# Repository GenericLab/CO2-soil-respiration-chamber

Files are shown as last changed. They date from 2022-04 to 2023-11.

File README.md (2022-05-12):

# CO2-soil-respiration-chamber

For more info of our developments and field testing, visit the hackeria wiki: https://www.hackteria.org/wiki/CO2_Soil_Respiration_Chamber

Visit our live data on Thingspeak: https://thingspeak.com/channels/1718702

## Make your own hardware

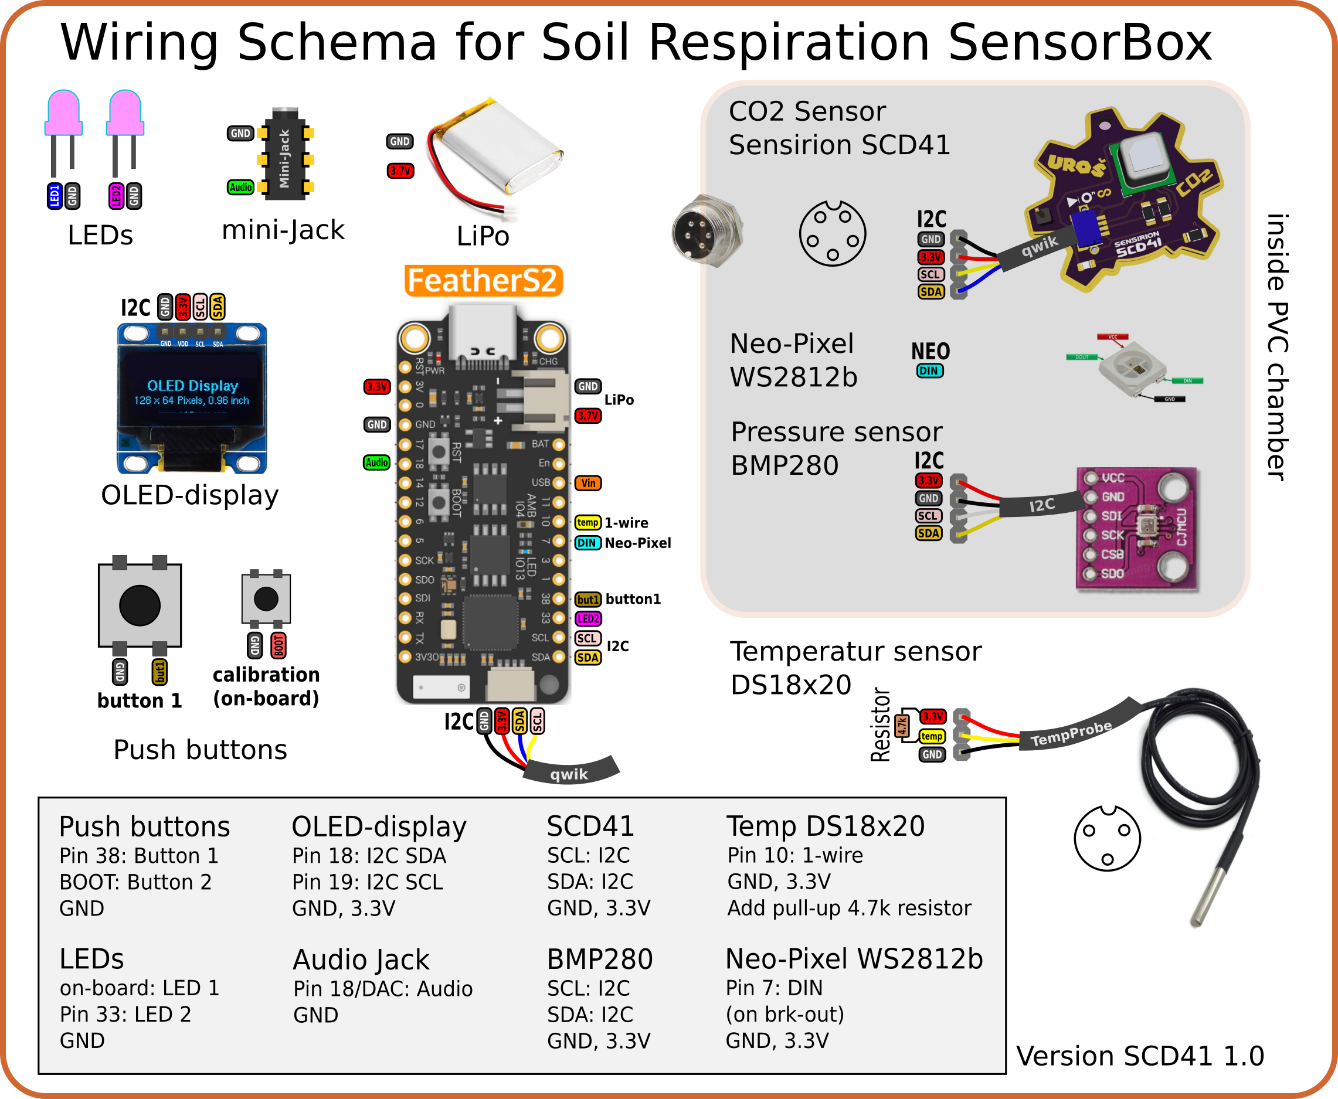
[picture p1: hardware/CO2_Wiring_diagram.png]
wiring diagram


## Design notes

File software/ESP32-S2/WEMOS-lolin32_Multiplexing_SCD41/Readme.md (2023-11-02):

This program allows to use up to four SCD41 with a Wemos lolin32 lite board for up to four soil respiration chambers to be running simultaneously, it includes the usage of a OLED screen as User Interface, a BMP280 sensor for altitude calibration, and data sending to two thingspeak channels.

The wiring is as shown next

Wemos_Schematics

You can acces the electrical details and PCB terminals count in the next file:
[Terminals Count](https://github.com/GenericLab/CO2-soil-respiration-chamber/blob/main/hardware/WEMOS-lolin32_Multiplexing_SCD41%20schematics/Terminals%20Count.xlsx)

The Soil respiration chamber contains a SCD41 sensor as shown next:

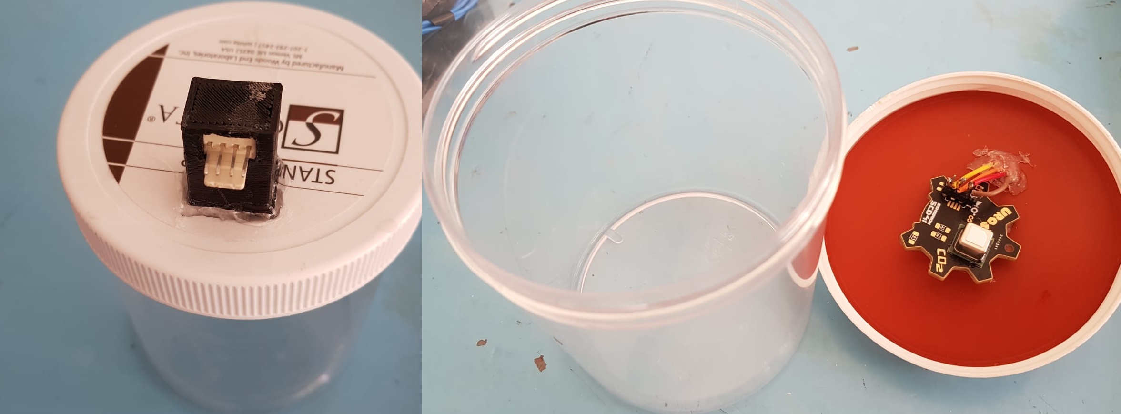
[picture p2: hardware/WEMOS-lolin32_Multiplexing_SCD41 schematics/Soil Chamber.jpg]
Soil Chamber 1


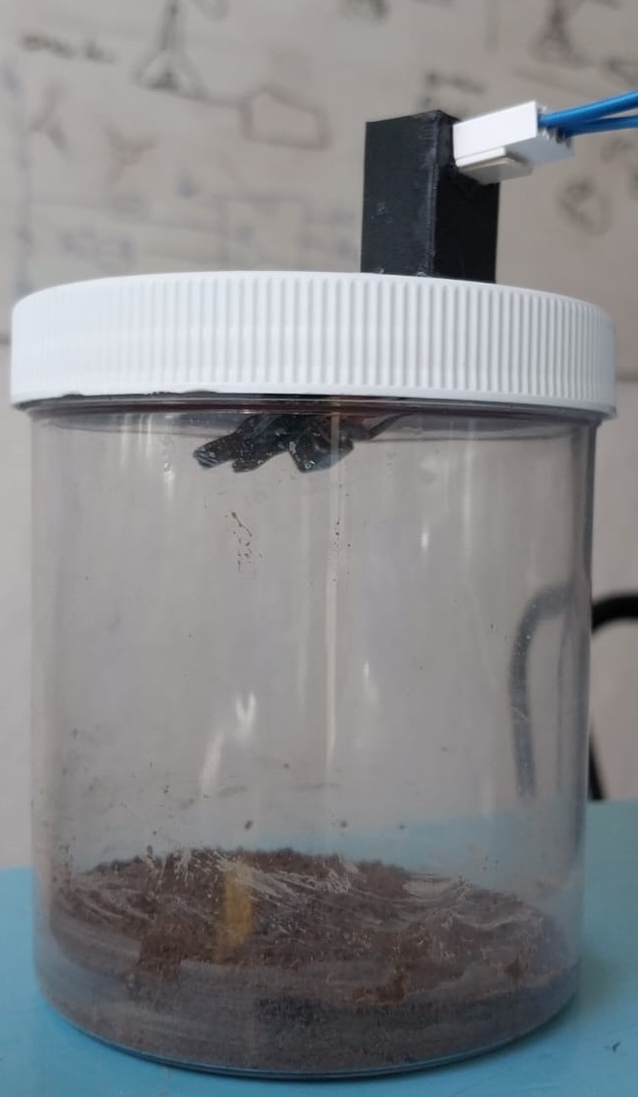
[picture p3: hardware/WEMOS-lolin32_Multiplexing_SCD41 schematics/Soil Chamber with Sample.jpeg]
Soil Chamber 2


The Cabinet that contains the rest of the electronics as shown next:

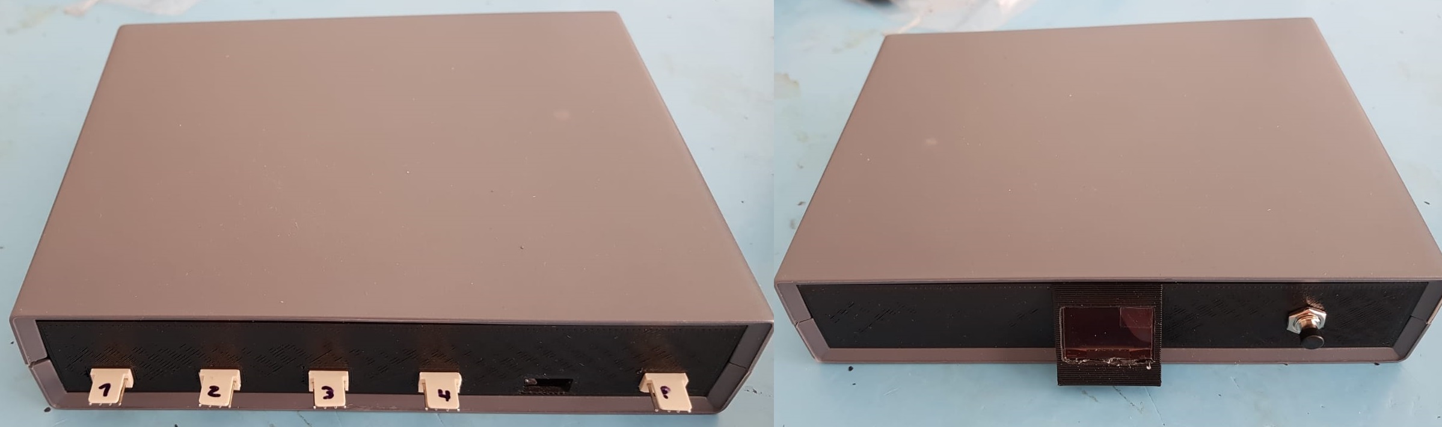
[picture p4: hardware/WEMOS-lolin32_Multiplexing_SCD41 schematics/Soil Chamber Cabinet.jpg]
Soil Chamber Cabinet 1


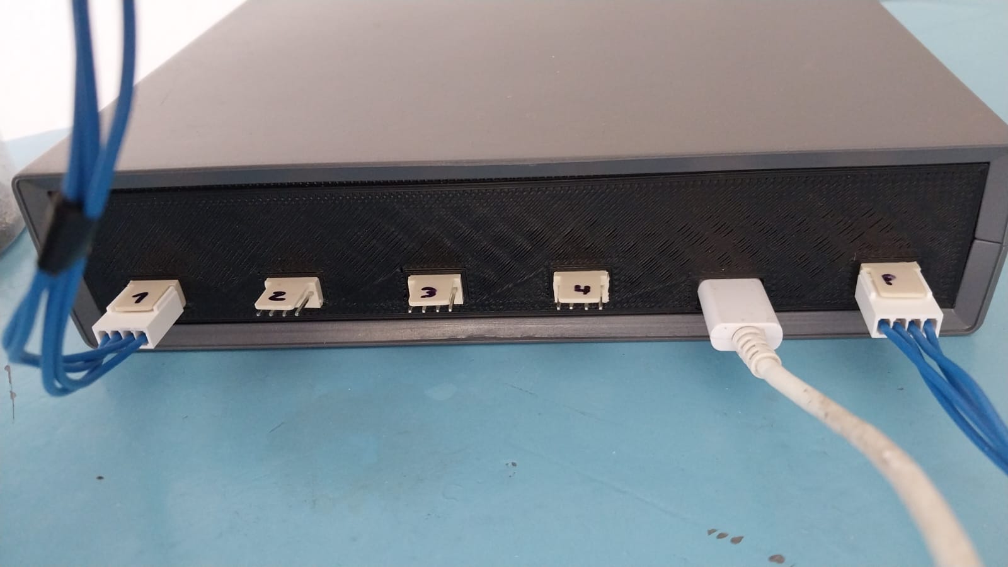
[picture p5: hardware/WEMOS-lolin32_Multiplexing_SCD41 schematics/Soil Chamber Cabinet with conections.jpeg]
Soil Chamber Cabinet 2


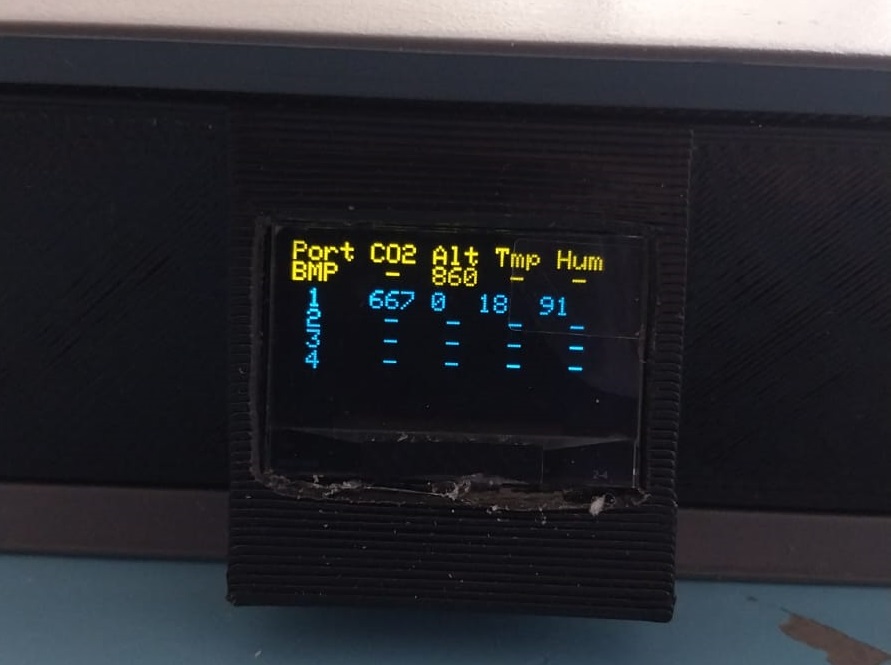
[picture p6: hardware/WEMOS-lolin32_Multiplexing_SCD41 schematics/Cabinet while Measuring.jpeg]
Soil Chamber Cabinet 3


The Wemos detects the sensors at setup, so you need to power the box after connecting the BMP280 (if available) and the SCD41 sensor

To start using the soil chamber you'll need to calibrate the sensor first. Then you shall weight 30 grams of the sample and slowly add 9 mililiters of water trying to hydrate most of the soil. Then you'll close the container and let it measuring the CO2 concentration, it is highly recomended to not turn off the readings, because the SCD41 can lose calibration when turned off.

The calibration procedure starts when the button is pressed for 5 seconds, this is for avoiding accidental pushes of the button such as bounce of vibrations. For calibration to be successfull you'll need to open the respiration chamber and expose the sensor and the chamber to fresh air, then push the buton so the sensor start to measure fresh air, it gets calibrated using the air pressure given by the BMP sensor if available, or the Lujan de Cuyo Altitude variable in SCD41_multiplexed.h file (you can change the used altitude in the main file istead of BMP readings if you need to). The full process last 3 to 4 minutes. After it's finished the sensor CO2 measurement is calibrated to 400 PPM, it is important to note that this is not an absolute measurement, but a relative one.

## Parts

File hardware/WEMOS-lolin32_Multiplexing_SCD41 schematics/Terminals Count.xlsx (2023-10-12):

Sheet: Terminals
 | Ground Pins | 3.3V Pins | I2C SCD Pins | I2C SDA Pins
Wemos Lolin32 Lite | 1 | 1 | 1 | 1
SCD41 | 4 | 4
Screen | 1 | 1 | 1 | 1
TCA9548A | 1 | 1 | 1 | 1
HW611 BMP280 | 1 | 1 | 1 | 1
Button | 1
 |  |  |  |  | Total
Total | 9 | 8 | 4 | 4 | 25

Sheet: Currents
 | mA | Quantity | Total mA | Fuente | Pagina
SCD41 | 15 | 4 | 60 | https://pdf1.alldatasheet.com/datasheet-pdf/view/1425096/SENSIRION/SCD41.html | 4
GME12864-43 | 12.3 | 1 | 12.3 | https://www.buydisplay.com/download/manual/ER-OLED0.96-1_Series_Datasheet.pdf | 14
TCA9548A | 0.05 | 1 | 0.05 | https://pdf1.alldatasheet.com/datasheet-pdf/view/463225/TI1/TCA9548A.html | 10
HW611 BMP280 | 0.0028 | 1 | 0.0028 | https://pdf1.alldatasheet.com/datasheet-pdf/view/1132069/BOSCH/BMP280.html | 7
 |  | Total | 72.3528
esp32 | 600 |  |  | https://learn.sparkfun.com/tutorials/esp32-thing-hookup-guide/hardware-overview
Cable Usb 3.0 | 500

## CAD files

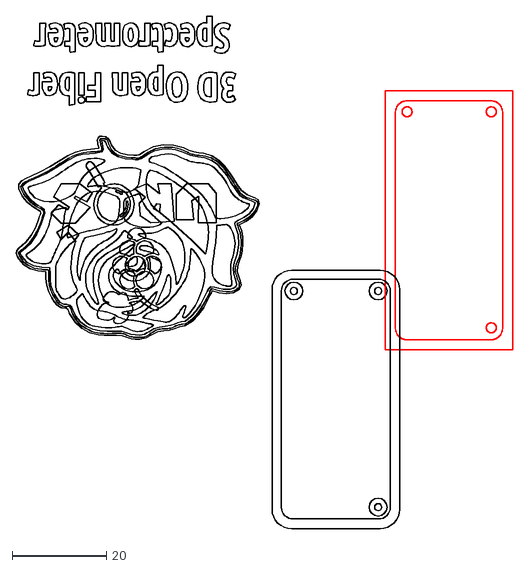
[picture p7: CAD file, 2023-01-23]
hardware/PVC-case/CO2_featherCase.dxf
105.6 x 109.0

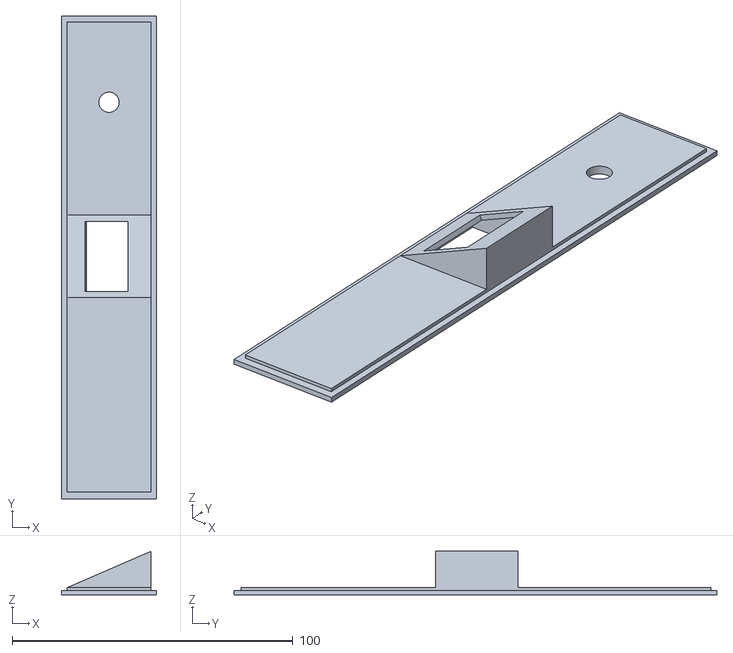
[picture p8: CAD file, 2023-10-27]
hardware/WEMOS-lolin32_Multiplexing_SCD41 schematics/3D models/Tapa posterior - pantalla.stl
34.0 x 172.0 x 15.5

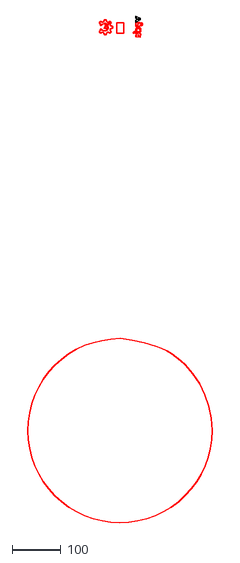
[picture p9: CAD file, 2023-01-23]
hardware/PVC-case/Logo_engravings.dxf
377.6 x 1037.0

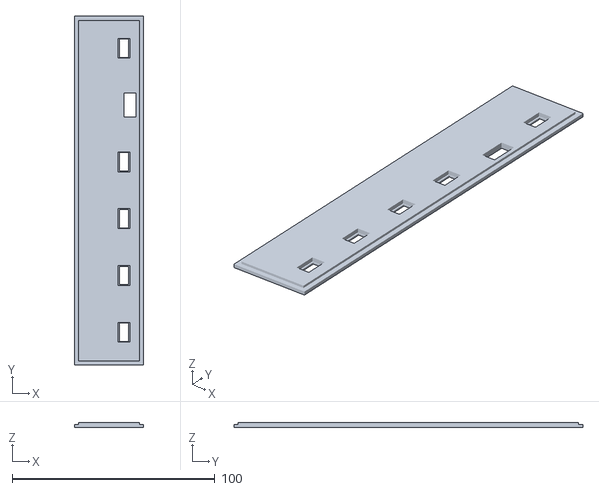
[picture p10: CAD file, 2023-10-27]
hardware/WEMOS-lolin32_Multiplexing_SCD41 schematics/3D models/Tapa anterior - conexiones.stl
34.0 x 172.0 x 2.50

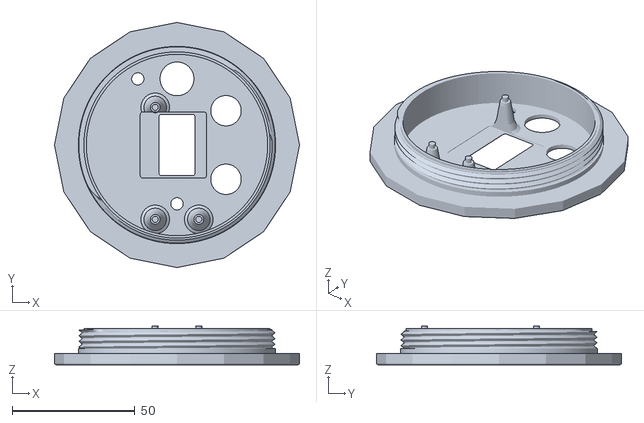
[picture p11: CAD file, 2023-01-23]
hardware/PVC-case/threaded_lid.stl
100.0 x 100.0 x 15.8

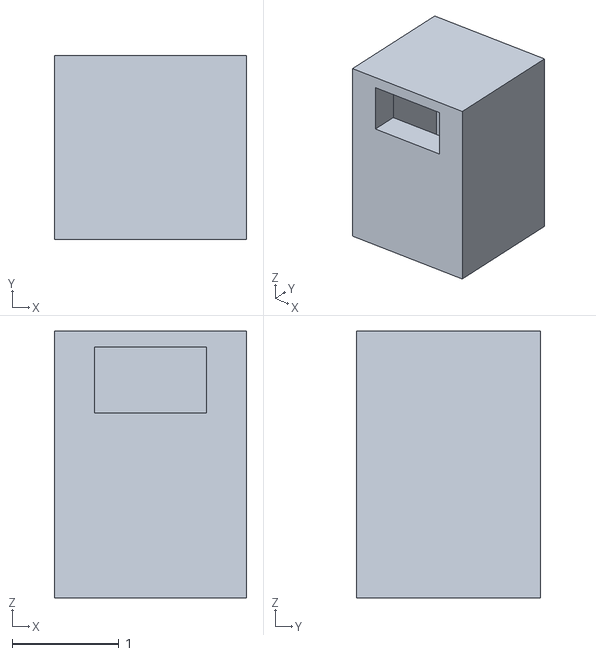
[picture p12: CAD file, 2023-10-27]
hardware/WEMOS-lolin32_Multiplexing_SCD41 schematics/3D models/Conexión Tapa.stl
1.80 x 1.73 x 2.50

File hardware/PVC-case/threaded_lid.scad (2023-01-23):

// 
// PVC piping threaded Lid for ROSA CO2 monitoring case
//
// This work is released with CC0 into the public domain.
// https://creativecommons.org/publicdomain/zero/1.0/
// based on work by  Ryan A. Colyer.
// https://www.thingiverse.com/thing:1686322
//

$fn=128;
wallThickness = 1.6;
engravingDepth = 0.6;
height = 2;

difference(){
union(){
minkowski(){    
cylinder(wallThickness-1.59, d = 100-1.6, center = true, $fn=16);
    sphere(d=1.6);
}
    
}
    translate([20,14,0]) rotate([0,0,0]) cylinder(h=100,d=12.4,center=true);
    translate([20,-14,0]) rotate([0,0,0]) cylinder(h=100,d=12.4,center=true);
    translate([-0,-24,0]) rotate([0,0,0]) cylinder(h=100,d=5,center=true);
    translate([-0,0,0.5*wallThickness+0.1]) rotate([0,180,0]) roundedRect2([14,24,1*wallThickness+0.2,1.2],1);
    translate([-1.5,0,1*wallThickness+0.7]) rotate([0,180,0]) roundedRect2([27,27,1*wallThickness+0.2,1],1);
    translate([-0,27,0]) rotate([0,0,0]) cylinder(h=100,d=13.8,center=true);
    translate([-16,27,0]) rotate([0,0,0]) cylinder(h=100,d=5,center=true);
    #translate([0,0,-1.5*wallThickness+engravingDepth]) linear_extrude(height =wallThickness, center = false, convexity = 10) import(file = "Logo_engravings.dxf", layer = "coconut");
    #translate([0,0,-1.5*wallThickness+engravingDepth]) linear_extrude(height =wallThickness, center = false, convexity = 10) import(file = "Logo_engravings.dxf", layer = "ROSA");
    
    
}


difference(){
    union(){
  translate([0,0,2]) ScrewThread(outer_diam=80, height=12, pitch=2.3, tooth_angle=40, tolerance=0.4, tip_height=0.5, tooth_height=2, tip_min_fract=0);
    translate([0,0,2.5+0.5*wallThickness]) cylinder(5, d = 80.5, center = true);
    
    translate([0,0,1.4+0.0*wallThickness]) cylinder(3, d = 100, center = true,$fn=16);
    translate([0,0,2.5+0.5*wallThickness]) cylinder(1, d = 100, center = true,$fn=16);
    translate([0,0,8]) cylinder(12, d = 76, center = true);
    }
    translate([0,0,0]) cylinder(50, d = 80-6, center = true);
}

difference(){
    translate([0,-7.5,-1]) rotate([0,0,180]) featherS2();
        translate([-1.5,0,1*wallThickness+10]) rotate([0,180,0]) roundedRect2([27,27,1*wallThickness+20,1],1);
}
 
module featherS2(){

    translate([8.89,22.86,6+0.5*wallThickness-0.1]) screwRod();
    translate([-8.89,22.86,6+0.5*wallThickness-0.1]) screwRod();
    translate([8.89,-22.86,6+0.5*wallThickness-0.1]) screwRod();

//linear_extrude(height = wallThickness, center = false, convexity = 10) import(file = "CO2_featherCase.dxf", layer = "base");
//linear_extrude(height =0, center = false, convexity = 10) import(file = "CO2_featherCase.dxf", layer = "border");
//linear_extrude(height = wallThickness + 1, center = false, convexity = 30) import(file = "CO2_featherCase.dxf", layer = "screws");
}

module screwRod (){
  difference(){
    union(){
     translate([0,0,1.3]) cylinder(12, d1 = 8, d2 = 4, center = true, $fn=30);
     translate([0,0,-1]) cylinder(8, d1 = 10, d2 = 3, center = true, $fn=30);
     translate([0,0,-4]) cylinder(2, d1 = 12, d2 = 6, center = true, $fn=30);
    }
    minkowski(){
    translate([0,0,3]) cylinder(10, d1 = 0.6, d2 = 0.8, center = true, $fn=3);
        sphere(r=0.8);
    }
  }
  translate([0,0,8])cylinder(2.5, d1 = 2.2, d2 = 2.5, center = true, $fn=30);
}





// Created 2016-2017 by Ryan A. Colyer.
// This work is released with CC0 into the public domain.
// https://creativecommons.org/publicdomain/zero/1.0/
//
// https://www.thingiverse.com/thing:1686322
//
// v2.1


screw_resolution = 0.2;  // in mm

// This generates a closed polyhedron from an array of arrays of points,
// with each inner array tracing out one loop outlining the polyhedron.
// pointarrays should contain an array of N arrays each of size P outlining a
// closed manifold.  The points must obey the right-hand rule.  For example,
// looking down, the P points in the inner arrays are counter-clockwise in a
// loop, while the N point arrays increase in height.  Points in each inner
// array do not need to be equal height, but they usually should not meet or
// cross the line segments from the adjacent points in the other arrays.
// (N>=2, P>=3)
// Core triangles:
//   [j][i], [j+1][i], [j+1][(i+1)%P]
//   [j][i], [j+1][(i+1)%P], [j][(i+1)%P]
//   Then triangles are formed in a loop with the middle point of the first
//   and last array.
module ClosePoints(pointarrays) {
  function recurse_avg(arr, n=0, p=[0,0,0]) = (n>=len(arr)) ? p :
    recurse_avg(arr, n+1, p+(arr[n]-p)/(n+1));

  N = len(pointarrays);
  P = len(pointarrays[0]);
  NP = N*P;
  lastarr = pointarrays[N-1];
  midbot = recurse_avg(pointarrays[0]);
  midtop = recurse_avg(pointarrays[N-1]);

  faces_bot = [
    for (i=[0:P-1])
      [0,i+1,1+(i+1)%len(pointarrays[0])]
  ];

  loop_offset = 1;
  bot_len = loop_offset + P;

  faces_loop = [
    for (j=[0:N-2], i=[0:P-1], t=[0:1])
      [loop_offset, loop_offset, loop_offset] + (t==0 ?
      [j*P+i, (j+1)*P+i, (j+1)*P+(i+1)%P] :
      [j*P+i, (j+1)*P+(i+1)%P, j*P+(i+1)%P])
  ];

  top_offset = loop_offset + NP - P;
  midtop_offset = top_offset + P;

  faces_top = [
    for (i=[0:P-1])
      [midtop_offset,top_offset+(i+1)%P,top_offset+i]
  ];

  points = [
    for (i=[-1:NP])
      (i<0) ? midbot :
      ((i==NP) ? midtop :
      pointarrays[floor(i/P)][i%P])
  ];
  faces = concat(faces_bot, faces_loop, faces_top);

  polyhedron(points=points, faces=faces);
}



// This creates a vertical rod at the origin with external threads.  It uses
// metric standards by default.
module ScrewThread(outer_diam, height, pitch=0, tooth_angle=30, tolerance=0.4, tip_height=0, tooth_height=0, tip_min_fract=0) {

  pitch = (pitch==0) ? ThreadPitch(outer_diam) : pitch;
  tooth_height = (tooth_height==0) ? pitch : tooth_height;
  tip_min_fract = (tip_min_fract<0) ? 0 :
    ((tip_min_fract>0.9999) ? 0.9999 : tip_min_fract);

  outer_diam_cor = outer_diam + 0.25*tolerance; // Plastic shrinkage correction
  inner_diam = outer_diam - tooth_height/tan(tooth_angle);
  or = (outer_diam_cor < screw_resolution) ?
    screw_resolution/2 : outer_diam_cor / 2;
  ir = (inner_diam < screw_resolution) ? screw_resolution/2 : inner_diam / 2;
  height = (height < screw_resolution) ? screw_resolution : height;

  steps_per_loop_try = ceil(2*3.14159265359*or / screw_resolution);
  steps_per_loop = (steps_per_loop_try < 4) ? 4 : steps_per_loop_try;
  hs_ext = 3;
  hsteps = ceil(3 * height / pitch) + 2*hs_ext;

  extent = or - ir;

  tip_start = height-tip_height;
  tip_height_sc = tip_height / (1-tip_min_fract);

  tip_height_ir = (tip_height_sc > tooth_height/2) ?
    tip_height_sc - tooth_height/2 : tip_height_sc;

  tip_height_w = (tip_height_sc > tooth_height) ? tooth_height : tip_height_sc;
  tip_wstart = height + tip_height_sc - tip_height - tip_height_w;


  function tooth_width(a, h, pitch, tooth_height, extent) =
    let(
      ang_full = h*360.0/pitch-a,
      ang_pn = atan2(sin(ang_full), cos(ang_full)),
      ang = ang_pn < 0 ? ang_pn+360 : ang_pn,
      frac = ang/360,
      tfrac_half = tooth_height / (2*pitch),
      tfrac_cut = 2*tfrac_half
    )
    (frac > tfrac_cut) ? 0 : (
      (frac <= tfrac_half) ?
        ((frac / tfrac_half) * extent) :
        ((1 - (frac - tfrac_half)/tfrac_half) * extent)
    );


  pointarrays = [
    for (hs=[0:hsteps])
      [
        for (s=[0:steps_per_loop-1])
          let(
            ang_full = s*360.0/steps_per_loop,
            ang_pn = atan2(sin(ang_full), cos(ang_full)),
            ang = ang_pn < 0 ? ang_pn+360 : ang_pn,

            h_fudge = pitch*0.001,

            h_mod =
              (hs%3 == 2) ?
                ((s == steps_per_loop-1) ? tooth_height - h_fudge : (
                 (s == steps_per_loop-2) ? tooth_height/2 : 0)) : (
              (hs%3 == 0) ?
                ((s == steps_per_loop-1) ? pitch-tooth_height/2 : (
                 (s == steps_per_loop-2) ? pitch-tooth_height + h_fudge : 0)) :
                ((s == steps_per_loop-1) ? pitch-tooth_height/2 + h_fudge : (
                 (s == steps_per_loop-2) ? tooth_height/2 : 0))
              ),

            h_level =
              (hs%3 == 2) ? tooth_height - h_fudge : (
              (hs%3 == 0) ? 0 : tooth_height/2),

            h_ub = floor((hs-hs_ext)/3) * pitch
              + h_level + ang*pitch/360.0 - h_mod,
            h_max = height - (hsteps-hs) * h_fudge,
            h_min = hs * h_fudge,
            h = (h_ub < h_min) ? h_min : ((h_ub > h_max) ? h_max : h_ub),

            ht = h - tip_start,
            hf_ir = ht/tip_height_ir,
            ht_w = h - tip_wstart,
            hf_w_t = ht_w/tip_height_w,
            hf_w = (hf_w_t < 0) ? 0 : ((hf_w_t > 1) ? 1 : hf_w_t),
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

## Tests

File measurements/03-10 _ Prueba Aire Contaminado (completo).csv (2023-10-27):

created_at | entry_id | field1 | field2 | field3 | field4 | field5
2023-10-03 15:27:58 UTC | 33 | 3388 | 65535 | 65535 | 65535 | 907
2023-10-03 15:28:30 UTC | 34 | 3389 | 65535 | 65535 | 65535 | 907
2023-10-03 15:29:01 UTC | 35 | 3389 | 65535 | 65535 | 65535 | 907
2023-10-03 15:29:32 UTC | 36 | 3389 | 65535 | 65535 | 65535 | 907
2023-10-03 15:30:03 UTC | 37 | 3389 | 65535 | 65535 | 65535 | 907
2023-10-03 15:30:33 UTC | 38 | 3388 | 65535 | 65535 | 65535 | 907
2023-10-03 15:31:04 UTC | 39 | 3388 | 65535 | 65535 | 65535 | 907
2023-10-03 15:31:35 UTC | 40 | 3387 | 65535 | 65535 | 65535 | 907
2023-10-03 15:32:05 UTC | 41 | 3385 | 65535 | 65535 | 65535 | 907
2023-10-03 15:32:36 UTC | 42 | 3384 | 65535 | 65535 | 65535 | 907
2023-10-03 15:33:07 UTC | 43 | 3384 | 65535 | 65535 | 65535 | 907
2023-10-03 15:33:38 UTC | 44 | 3377 | 65535 | 65535 | 65535 | 907
2023-10-03 15:34:08 UTC | 45 | 3377 | 65535 | 65535 | 65535 | 908
2023-10-03 15:34:39 UTC | 46 | 3375 | 65535 | 65535 | 65535 | 907
2023-10-03 15:35:10 UTC | 47 | 3373 | 65535 | 65535 | 65535 | 907
2023-10-03 15:35:41 UTC | 48 | 3377 | 65535 | 65535 | 65535 | 907
2023-10-03 15:36:11 UTC | 49 | 3374 | 65535 | 65535 | 65535 | 907
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

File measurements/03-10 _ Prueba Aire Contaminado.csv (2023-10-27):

created_at | entry_id | field1
2023-10-03 15:27:28 UTC | 32 | 3388
2023-10-03 15:27:58 UTC | 33 | 3388
2023-10-03 15:28:30 UTC | 34 | 3389
2023-10-03 15:29:01 UTC | 35 | 3389
2023-10-03 15:29:32 UTC | 36 | 3389
2023-10-03 15:30:03 UTC | 37 | 3389
2023-10-03 15:30:33 UTC | 38 | 3388
2023-10-03 15:31:04 UTC | 39 | 3388
2023-10-03 15:31:35 UTC | 40 | 3387
2023-10-03 15:32:05 UTC | 41 | 3385
2023-10-03 15:32:36 UTC | 42 | 3384
2023-10-03 15:33:07 UTC | 43 | 3384
2023-10-03 15:33:38 UTC | 44 | 3377
2023-10-03 15:34:08 UTC | 45 | 3377
2023-10-03 15:34:39 UTC | 46 | 3375
2023-10-03 15:35:10 UTC | 47 | 3373
2023-10-03 15:35:41 UTC | 48 | 3377
2023-10-03 15:36:11 UTC | 49 | 3374
2023-10-03 15:36:42 UTC | 50 | 3367
2023-10-03 15:37:13 UTC | 51 | 3368
2023-10-03 15:37:44 UTC | 52 | 3363
2023-10-03 15:38:17 UTC | 53 | 3364
2023-10-03 15:38:48 UTC | 54 | 3364
2023-10-03 15:39:19 UTC | 55 | 3367
2023-10-03 15:39:50 UTC | 56 | 3365
2023-10-03 15:40:20 UTC | 57 | 3362
2023-10-03 15:40:54 UTC | 58 | 3368
2023-10-03 15:41:24 UTC | 59 | 3368
2023-10-03 15:41:55 UTC | 60 | 3366
2023-10-03 15:42:26 UTC | 61 | 3367
2023-10-03 15:42:57 UTC | 62 | 3367
2023-10-03 15:43:27 UTC | 63 | 3366
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

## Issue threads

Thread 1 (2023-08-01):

### ISSUE TITLE
Read the SDA51 through the MUX

### ISSUE THREAD

**Issue by MaximilianoGarcia716** [GenericLab/CO2-soil-respiration-chamber#1]
The MUX and the WEMOS recognize the SDA51, now the WEMOS need to read it

**Comment by nanocastro** [comment]
this to read several CO2 sensors with the same device

**Comment by MaximilianoGarcia716** [comment]
The sensors can be readed through the multiplexer. The code is getting more compact and modular.

**Comment by MaximilianoGarcia716** [comment]
Can be seen resolved in file CO2-soil-respiration-chamber/software/ESP32-S2/WEMOS-lolin32_Multiplexing_SCD41/

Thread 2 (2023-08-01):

### ISSUE TITLE
Add a CO2 sensor calibration routine 

### ISSUE THREAD

**Issue by nanocastro** [GenericLab/CO2-soil-respiration-chamber#2]
CO2 sensors are usually calibrated in an open environment atmosphere and the co2 concentration is supposed to be 400ppm. 
We don't need a precise absolute value because in respiration we are looking at relative values but we need to think of a way to enter calibration mode (extra button...?) and a protocol. I think the easiest solution is to enter calibration mode and then put all sensors at once in free air for a while (5min/10 mins) and then store the last value (or make a median of the few last values)

**Comment by MaximilianoGarcia716** [comment]
The calibration routine is ready, it is entered when push the calibration button and use the calibration algorithm suggested by the datasheet

**Comment by MaximilianoGarcia716** [comment]
Can be seen resolved in CO2-soil-respiration-chamber/software/ESP32-S2/WEMOS-lolin32_Multiplexing_SCD41/

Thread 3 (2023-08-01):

### ISSUE TITLE
CO2 sensor altitude setting

### ISSUE THREAD

**Issue by nanocastro** [GenericLab/CO2-soil-respiration-chamber#3]
We need to be sure to set the right altitude to all CO2 sensors. See [datasheet](https://sensirion.com/products/catalog/SCD42/) for this. Maybe this also needs a reoutine to be changed if the sensors/device change location but for the moment we can add it directly to the code

**Comment by MaximilianoGarcia716** [comment]
Can be seen resolved in CO2-soil-respiration-chamber/software/ESP32-S2/WEMOS-lolin32_Multiplexing_SCD41/

**Comment by MaximilianoGarcia716** [comment]
Can be seen resolved in CO2-soil-respiration-chamber/software/ESP32-S2/WEMOS-lolin32_Multiplexing_SCD41/

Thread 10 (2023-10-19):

### ISSUE TITLE
Calculate the supported and used current of the devices

### ISSUE THREAD

**Issue by MaximilianoGarcia716** [GenericLab/CO2-soil-respiration-chamber#10]
Calculate the supported current of the wemos lolin32 liteand the USB cable. Also is necesary to estimate the charge usage of all the devices to avoid electrical issues.

**Comment by MaximilianoGarcia716** [comment]
Used current calculated, yet not uploaded

**Comment by nanocastro** [comment]
hola Maxi. porfa empecemos a completar esto con links fotos o lo que haga falta para que se entienda. si es en castellano no importa mientras este

**Comment by MaximilianoGarcia716** [comment]
Added in:
https://github.com/GenericLab/CO2-soil-respiration-chamber/blob/main/hardware/WEMOS-lolin32_Multiplexing_SCD41%20schematics/Terminals%20Count.xlsx

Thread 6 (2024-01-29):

### ISSUE TITLE
Add documentation to code and to readme

### ISSUE THREAD

**Issue by MaximilianoGarcia716** [GenericLab/CO2-soil-respiration-chamber#6]
Add documetation to the code in form of comments and add info in the readme in form of images and explanations.

**Comment by MaximilianoGarcia716** [comment]
Code is more commented than before, not step by step, but commented at least to tell what every function does

**Comment by nanocastro** [comment]
vayamos pensando en hacer un readme que explique el diseño general, workflow, librerias etc. podemos hacer un markdown y dp subirlo o como prefieran  
esta bueno que no esperen a terminar para subirlo. si lo linkean aca todes podemos ir colaborando   
@Santi-Uriguen estemos atentos a ir haciendo esto con todos los experimentos que hagamos

**Comment by MaximilianoGarcia716** [comment]
Code is commented, working on readme.md

**Comment by MaximilianoGarcia716** [comment]
Readme ready

**Comment by MaximilianoGarcia716** [comment]
Add workflow and libraries

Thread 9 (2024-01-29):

### ISSUE TITLE
Create a chassis and cable blueprint

### ISSUE THREAD

**Issue by MaximilianoGarcia716** [GenericLab/CO2-soil-respiration-chamber#9]
It is needed to create a chassis and cable blueprint to create the conexions and layout of the devices.

**Comment by nanocastro** [comment]
suban aca lo que han hecho, lista de materiales, fotos y si hay diseños tambien (stl y editables)

**Comment by nanocastro** [comment]
estaría bueno también preparar el segundo recipiente. una sugerencia para el adaptador de la tapa 
![imagen](https://github.com/GenericLab/CO2-soil-respiration-chamber/assets/23299935/78cdaf3a-4085-48f8-a239-4e6f27f3afed)

**Comment by MaximilianoGarcia716** [comment]
Ya subimos al repositorio el diagrama del circuito, está en el enlace:
https://github.com/GenericLab/CO2-soil-respiration-chamber/blob/main/hardware/WEMOS-lolin32_Multiplexing_SCD41%20schematics/Lolin%20Multiplexing.png

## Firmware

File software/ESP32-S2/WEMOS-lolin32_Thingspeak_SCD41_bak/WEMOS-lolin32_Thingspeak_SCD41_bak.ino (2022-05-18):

 /*
 * dusjagr edited some stuffs...
 * Adding display
 * Adding timer
 * Adding BMP280 pressure sensor
 * Adding Neo-Pixel on pin 18
 * Adding Dallas Temperature sensor for external use of soil temperature probe
 * different version of OneWireNG had to be used to compile correctly on ESP32 S2
 * Not finished: proper calibration routine
 * 
 */


//#define FEATHERS2
#define WEMOS_LOLIN32

#define SCD41_IS_ATTACHED
//#define BMP_IS_ATTACHED
//#define DS18x20_IS_ATTACHED
#define USE_THINGSPEAK

#ifdef USE_THINGSPEAK
  #include "/home/dusjagr/secrets.h"
#endif

#include <Arduino.h>
#include <SensirionI2CScd4x.h>
#include <Wire.h>
#include <Adafruit_NeoPixel.h>
#include "OLED_stuff.h"

#ifdef WEMOS_LOLIN32 // LITE
const int LEDonBoard = 22;       // the number of the LED pin
const int LEDexternal = 2;      // the number of the LED pin
const int buttonPin = 14;        // the number of the pushbutton pin
const int cal_pin = 12;           // entrada pulsador calibración
const int neoPixelPin = 2;          // NeoPixel for UROS board
#define SDA_PIN 5
#define SCL_PIN 18
#endif

#ifdef FEATHERS2
const int LEDonBoard = 13;       // the number of the LED pin
//const int LEDexternal = 33;      // the number of the LED pin
const int LEDexternal = 21;      // 2nd LDO on GPIO21
const int buttonPin = 38;        // the number of the pushbutton pin
const int cal_pin = 0;           // entrada pulsador calibración
const int neoPixelPin = 7;          // NeoPixel for UROS board
#define SDA_PIN 13
#define SCL_PIN 14
#endif

int ledState = LOW;              // ledState used to set the LED
int buttonState = HIGH;          // the current reading from the input pin
int lastButtonState = HIGH;      // the previous reading from the input pin
int screenState = 0;             // different views on the OLED screen

unsigned long lastDebounceTime = 0;  // the last time the output pin was toggled
unsigned long debounceDelay = 50;    // the debounce time; increase if the output flickers

const int neoPixelcount = 1;         // How many NeoPixels are attached?
int neoBrightness = 25;

  float BMP280temp = -1;
  float BMP280preshPa = -1;
  float soilTemperatureC = -1;
  uint32_t BMP280pres = -1;
  float BMP280alti = -1;

// Declare our NeoPixel object:
Adafruit_NeoPixel neopixel(neoPixelcount, neoPixelPin, NEO_GRB + NEO_KHZ800);

// OLED stuffs **********************
// ==================================

#include <Adafruit_GFX.h>
#include <Adafruit_SSD1306.h>

#define OLED_RESET 4
#define SCREEN_ADDRESS 0x3C //
#define SCREEN_WIDTH 128 // OLED display width, in pixels
#define SCREEN_HEIGHT 64 // OLED display height, in pixels
uint32_t displayLimit = 1500;
uint32_t displayLowerLimit = 0;
uint32_t displayFactor = (displayLimit-displayLowerLimit) / 48;
uint32_t meas_counter = 0;
int32_t thresholdPPM = 450;

// Declare our display object:
Adafruit_SSD1306 display(SCREEN_WIDTH, SCREEN_HEIGHT, &Wire, OLED_RESET);


// SCD41 calibration settings *******
// ==================================

uint16_t alt = 132;
uint32_t pressureCalibration;
float tempOffset = 2.0;
bool ascSetting = false; // Turn automatic self calibration off

// DS18x20 stuffs *******************
// ==================================

#ifdef DS18x20_IS_ATTACHED
  #include <OneWireNg_Config.h>
  #include <OneWireNg_BitBang.h>
  #include <OneWireNg_CurrentPlatform.h>
  #include <OneWireNg.h>
  #include <DallasTemperature.h>

  // GPIO where the DS18B20 is connected to
  const int oneWireBus = 10;  
  unsigned long DS18x20DataTimer = 0;   
  OneWire oneWire(oneWireBus);
  DallasTemperature DS18x20sensors(&oneWire);
  // arrays to hold device address
  DeviceAddress soilThermometer;

  //float soilTemperatureC;

  // function to print a device address
void printAddress(DeviceAddress deviceAddress)
{
  for (uint8_t i = 0; i < 8; i++)
  {
    if (deviceAddress[i] < 16) Serial.print("0");
    Serial.print(deviceAddress[i], HEX);
  }
}
#endif

// BMP280 stuffs ********************
// ==================================

#ifdef BMP_IS_ATTACHED
  #include <Adafruit_BMP280.h>
  Adafruit_BMP280 bmp; // I2C

  #define SEA_LEVEL_PRESSURE    1010.0f   // sea level pressure 1013.25
  #define BMP_ADDRESS 0x76
  //float BMP280temp;
  //uint32_t BMP280pres;
  //float BMP280preshPa;
  //float BMP280alti;
  unsigned long BMP280DataTimer = 0;
#endif

// Sensirion SCD4x stuffs ***********
// ==================================

SensirionI2CScd4x scd4x;

unsigned long SCD41DataTimer = 0;
unsigned long TimeSec = 0;
unsigned long timeElapse = 0;//used to wait the sensor to stabilize before calibration
uint16_t error;
char errorMessage[256];
uint16_t co2;
float temperature;
float humidity;

void printUint16Hex(uint16_t value) {
    Serial.print(value < 4096 ? "0" : "");
    Serial.print(value < 256 ? "0" : "");
    Serial.print(value < 16 ? "0" : "");
    Serial.print(value, HEX);
}

void printSerialNumber(uint16_t serial0, uint16_t serial1, uint16_t serial2) {
    Serial.print("Serial: 0x");
    printUint16Hex(serial0);
    printUint16Hex(serial1);
    printUint16Hex(serial2);
    Serial.println();
}


// THINGSSPEAK ********************
// ==================================

#ifdef USE_THINGSPEAK
  #include <WiFi.h>
  #include "ThingSpeak.h" // always include thingspeak header file after other header files and custom macros
  
  char ssid[] = SECRET_SSID;   // your network SSID (name) 
  char pass[] = SECRET_PASS;   // your network password
  int keyIndex = 0;            // your network key Index number (needed only for WEP)
  WiFiClient  client;
  unsigned long thingspeakDataTimer = 0;
  unsigned long myChannelNumber = SECRET_CH_ID;
  const char * myWriteAPIKey = SECRET_WRITE_APIKEY;

void connectWifi(){
    // Connect or reconnect to WiFi
    if(WiFi.status() != WL_CONNECTED){
      OLEDtestWiFi();
      neopixel.setPixelColor(0, neopixel.Color(0, 0, 255));
      neopixel.show();
      Serial.print("Attempting to connect to SSID: ");
      Serial.println(SECRET_SSID);
      while(WiFi.status() != WL_CONNECTED){
        WiFi.begin(ssid, pass);  // Connect to WPA/WPA2 network. Change this line if using open or WEP network
        Serial.print(".");
        delay(2000);
        neopixel.setPixelColor(0, neopixel.Color(255, 0, 0));
        neopixel.show();
        delay(2000);
        neopixel.clear();
        neopixel.show();     
      } 
      Serial.println("\nConnected.");
      neopixel.setPixelColor(0, neopixel.Color(0, 255, 0));
      neopixel.show();
      OLEDtestSuccess();
      delay(2000);
      OLEDdrawBackground();
    }
}
  
#endif

void setup() {
    
    Serial.begin(115200);
    //while ( !Serial ) delay(100);   // wait for native usb
    delay(500);
    Serial.println("    ");
    Serial.println("=========== Booting ROŠA System ===========");
    pinMode(LEDonBoard, OUTPUT);
    digitalWrite(LEDonBoard, HIGH);
    pinMode(LEDexternal, OUTPUT);
    digitalWrite(LEDexternal, HIGH);
    pinMode(buttonPin, INPUT_PULLUP);
    pinMode(cal_pin, INPUT_PULLUP); // entrada pulsado para calibrar, seteada como pulluppara poder conectar pulsador sin poenr resistencia adicional
    
    Serial.println("    ");
    Serial.println("=========== start Wire i2c ==================");
    #ifdef WEMOS_LOLIN32
    Wire.begin(SDA_PIN, SCL_PIN);
    #endif
    #ifdef FEATHERS2
    Wire.begin();
    #endif
    Serial.println("    ");
    Serial.println("=========== Initializing OLED Screen ===========");
    initDisplay();
    Serial.println("    ");
    delay(100);

    showLogo_hackteria();
    delay(1000);

    showLogo_regosh();
    delay(1000);
    showLogo_humus_text();
    delay(1000);

    display.clearDisplay();

    Serial.println("    ");
    Serial.println("=========== Turn on NEO Pixel ==================");
    neopixel.begin();           // INITIALIZE NeoPixel strip object (REQUIRED)
    delay(100);
    neopixel.clear();
    neopixel.show();
    neopixel.setBrightness(neoBrightness); // Set BRIGHTNESS to about 1/5 (max = 255)

    //rainbow(5);             // Flowing rainbow cycle along the whole strip
    //rainbowCycle(5);
    neopixel.setPixelColor(0, neopixel.Color(255, 0, 255));
    neopixel.show();    
    Serial.println("    ");
    Serial.println("=========== Turn on Wifi ==================");

#ifdef USE_THINGSPEAK
    WiFi.mode(WIFI_STA);   
    ThingSpeak.begin(client);  // Initialize ThingSpeak
    Serial.println("Starting WiFi");
    neopixel.clear();
    neopixel.show();
    connectWifi();
#endif

    Serial.println("    ");

    Serial.println("============ Testing DS18x20 Sensor ============");

// needs to be finished
//*****************************************
#ifndef DS18x20_IS_ATTACHED
    Serial.println("DS18x20 not in use");
    OLEDtestDS18b20();
    delay(500);
    OLEDnotinuse();
    delay(2000);
#endif

#ifdef DS18x20_IS_ATTACHED
    Serial.println("DS18x20: begin");
    OLEDtestDS18b20();
    DS18x20sensors.begin();

    Serial.print("DS18x20: Found ");
    Serial.print(DS18x20sensors.getDeviceCount(), DEC);
    Serial.println(" devices.");

    if (!DS18x20sensors.getAddress(soilThermometer, 0)) {
      Serial.println("Unable to find address for Device 0");
      delay(500);
      showError(); //ERROR
    } else {
      delay(500);
      OLEDtestSuccess();
    }

    Serial.print("DS18x20: Device 0 Address: ");
    printAddress(soilThermometer);
    Serial.println();

    // set the resolution to 9 bit (Each Dallas/Maxim device is capable of several different resolutions)
    DS18x20sensors.setResolution(soilThermometer, 12);
 
    Serial.print("DS18x20: Device 0 Resolution: ");
    Serial.print(DS18x20sensors.getResolution(soilThermometer), DEC); 
    Serial.println();
    
    DS18x20sensors.requestTemperatures(); 
    soilTemperatureC = DS18x20sensors.getTempCByIndex(0);
    Serial.println("DS18x20: read once:");
    Serial.print("Soil Temperature: ");
    Serial.print(soilTemperatureC);
    Serial.println(" ºC");
    delay(1000);

    Serial.println("==================  end test  ==================");
    Serial.println();
#endif

    Serial.println("======== Testing BMP280 Pressure Sensor ========");
    
#ifndef BMP_IS_ATTACHED
    Serial.println("BMP280 not in use");
    OLEDtestBMP280();
    delay(500);
    OLEDnotinuse();
    delay(2000);
#endif
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

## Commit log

2022-04-26 adding wiring diagram
2022-05-09 adding other ESP boards
2022-05-18 small improvements
    [3inch_Lid.scad, 3inch_Lid.stl]
2023-01-23 compatible with ESP-S3 and added OTA support
    [CO2_featherCase.dxf, Logo_engravings.dxf, threaded_lid.scad, threaded_lid.stl]
2023-10-26 Uploading 3D case models
    [Conexión Tapa.stl, Tapa anterior - conexiones.stl, Tapa posterior - pantalla.stl]
2023-10-26 Create "measurements" folder and upload tests
    [03-10 _ Prueba Aire Contaminado (completo).csv, 03-10 _ Prueba Aire Contaminado.csv, 03-10 _ Prueba Aire Limpio (completo).csv, 03-10 _ Prueba Aire Limpio.csv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]
